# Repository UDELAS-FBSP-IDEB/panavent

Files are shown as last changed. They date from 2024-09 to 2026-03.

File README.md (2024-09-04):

# Panavent Project - An Open-Source Mechanical Ventilator.

This repository contains all the essential components for designing and implementing a mechanical ventilator. The central component is a gas mixer for mechanical ventilators, utilizing a multiloop and parallel PID controller system. The design and control system for the expiratory valve are also included, along with a C# application to manage the device's behavior, define various respiratory parameters, and display flow, volume, and pressure graphs.

The project provides a comprehensive solution, including hardware designs, control algorithms, 3D models, and complete source code for easy replication and further development.

## Project Structure

The repository is structured as follows:

- `/Electronics`: Contains electronic circuit schematics and hardware design files used in the gas mixer.
- `/3DModels`: 3D models and designs for the components used in the gas mixer.
- `/SourceCode`: The full code used for the control system, designed to run on the embedded platform.

## Features

- **Precise Gas Mixing**: Achieved using PID controllers in a multiloop and parallel configuration.
- **Open Source**: All designs, code, and models are provided as open-source materials.
- **Comprehensive**: Includes electronic design, mechanical components, and the full control algorithm.
- **Replicable**: All components can be replicated and adapted for various applications in medical settings.

## Requirements

- MPLAB X IDE and a PICkit programmer for executing the code of the microcontroller.
- Visual Studio 2017 or later for compiling and running the PC software.
- 3D printer for generating the physical components.
- Basic knowledge of PID control systems and electronics.
  
## License
This project is licensed under the MIT License, allowing for open-source distribution and adaptation. Please credit the original authors when using or adapting this work.

## Contact
For any questions or further information, feel free to reach out at luys.santana.0@udelas.ac.pa

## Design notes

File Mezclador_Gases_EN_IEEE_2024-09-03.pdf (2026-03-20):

Abstract-- Objective: To design and implement a gas mixer for mechanical ventilators using a system of PID controllers in multiloop and parallel configuration. Methods: The design process included addressing the theoretical principles of gas mixing by partial volumes and their relationship with mechanical ventilation parameters. The electro-pneumatic system of the mixer, the control system, and its implementation were developed and documented in detail. Results: The system's performance was
evaluated | through | experimental | tests, | and | the | results
demonstrated effective control and reliable gas mixing according to the set parameters. Conclusion: The proposed design successfully achieves the intended gas mixing for mechanical ventilators, ensuring accurate and consistent gas delivery. Significance: This work provides a comprehensive solution,
including | all | electronic | designs, | 3D | components, | and
programming code, contributing to the advancement of mechanical ventilation technology.

Index Terms-- Mechanical ventilation, gas mixer, PID
controllers, | multiloop | configuration, | parallel | control,
experimental prototype.
I. INTRODUCTION

The gas mixer in a mechanical ventilator plays a crucial role in preparing the therapeutic mixture of air and oxygen that is delivered to the patient during treatment. Its primary function is to accurately adjust the oxygen volume fraction (FiO2) in the inhaled gas mixture according to the specific needs of the patient. Additionally, the gas mixer actively participates in regulating the gas flow, taking into account parameters such as respiratory rate, airway pressure, and the set tidal volume. Precise control of these parameters is essential to ensure appropriate treatment, minimize the risks associated with
mechanical | ventilation, | and | ensure | the | successful
implementation of the therapeutic strategy defined by the attending physician [1], [2], [3].

The technical characteristics of the gas mixer are defined based on the specifications of the mechanical ventilator and its performance. In 2020, the World Health Organization suggested the minimum requirements for mechanical ventilators used in the treatment of acute respiratory diseases such as COVID-19 [4]; among these requirements, it is mentioned that an ICU mechanical ventilator should be able to regulate FiO2 between 21% and 100%, produce inspiratory flows from 1 to 160 L/min, and be compatible with both high and low-pressure oxygen sources. These requirements directly apply to the gas mixing module of the ventilator, as it is responsible for managing these aspects in the mechanical ventilator.

Given the importance of the gas mixer in a mechanical ventilator, numerous studies have focused on its optimization. Soares et al. [5] conducted a comprehensive review of the different types of gas mixers used in mechanical ventilators, highlighting the implementation of Proportional-Integral-Derivative (PID) controllers to regulate the air and oxygen mixture. Taube [6] describes an air and oxygen mixing system that uses a proportional solenoid valve, controlled by a microprocessor to automatically adjust the FiO2 according to the patient's blood oxygen saturation. Additionally, Taube [7] presents a system that not only mixes but also heats and humidifies the gases, with an adaptive PID control that adjusts the oxygen mixture delivered to the patient according to their needs. Radzi et. al [8] implemented a prototype that regulates the inspired oxygen fraction (FiO2) using proportional flow control valves for air and oxygen, integrating sensors that allow dynamic adjustment of the gas flow.

While gas mixing systems that use PID controllers are a well-established technology, there is limited documentation on the use of multiloop controllers in this context. This study describes the design and implementation of an advanced gas mixing system aimed at applications in mechanical ventilation. A system has been developed that employs PID controllers organized in a multiloop and parallel configuration, designed to keep the control functions of different hardware aspects separate, under the premise that this separation of roles optimizes the overall system's precision and stability. In this regard, our development focuses on independently managing the individual flow of each gas through the implementation of cascaded control subsystems, where the output of one controller serves as the input for the next. This approach aligns with previous research that has demonstrated the effectiveness of

Luys R. Santana, Manuel M. Batista, Sorhay M. Vásquez Biomedical Research and Development Center (IDEB) Faculty of Biosciences and Public Health, Universidad Especializada de las Américas (UDELAS), Paseo de la Iguana, Albrook, Panama City, Republic of Panama.

# Experimental prototype of an open-source gas mixer for mechanical ventilation based on PID controllers in

multiloop and parallel configuration.

dual systems in mechanical ventilation, where different loops effectively manage various respiratory parameters [9].

This document is structured as follows: first, the theoretical foundations of gas mixing are described, defining the mathematical framework that underpins the prototype. Next, the conceptual design is presented, and the control schemes used are explained. Then, the implementation of the device is detailed, along with its performance metrics. All electronic designs, 3D components, and the complete program code are provided. Finally, an exhaustive analysis of the obtained results is offered.

II. THEORETICAL FOUNDATIONS OF GAS MIXING
Amagat's Law of Partial Volumes states that in a mixture of gases, the total volume of the mixture is equal to the sum of the individual volumes of each of the gases that make up the mixture, as if they were coexisting separately at the same temperature and pressure [10]. Mathematically, it is expressed as:

Vt = ∑ Vi

n
i=1 = V1 + V2 + ⋯ + Vn

1 = ∑

Vi
Vt

n
i=1

(1)

where Vt
corresponds to the total volume in the mixture of n gases. Consequently, the volume of each gas corresponds to a fraction of the total volume, such that their sum equals one.

In this context, air itself constitutes a mixture of different gases, with oxygen present at a concentration of 21% (typically at sea level), along with other gases such as nitrogen and argon, which together make up the remaining 79%. Applying equation (1), we can represent this mixture as follows:

VM = 0.79VM + 0.21VM | (2)

where VM is the total volume of the mixture, 0.21VM is the total volume of oxygen, and 0.79VM is the volume of the other components.

If one wished to prepare a mixture of oxygen-enriched air (air that receives an additional supply of oxygen) with a total volume VM and an arbitrary oxygen concentration CM defined in the range 0.21 ≤ CM ≤ 1, it would be understood that:

VM = 0.79Vair + Vto2
(4)

where Vair is the volume of air added to the mixture and Vto2 is the total volume of oxygen:

Vto2 = 0.21Vair + Vo2
(5)

where Vo2
is the volume of additional pure oxygen.

On the other hand, by applying equation (2), it can be deduced that the oxygen concentration CM in the mixture VM is given by:

CM =

Vto2
VM

(6)

so that:

Vto2 = CM. VM | (7)

The concentration of the other gases would be given by:

0.79Vair = (1 − CM)VM

Vair =

(1−CM)VM
0.79 | (8)

while the volume of oxygen Vo2 :

Vto2 = 0.21Vair + Vo2 = CMVM

Vo2 = CMVM − 0.21Vair | (9)

Directly measuring the volume can be impractical in this type of application, so we could redefine these formulas in terms of flow if we consider that VM must be delivered during the inspiratory phase of ventilation, which has a duration Ti .
Thus, we can define a target flow FM as:

FM =

VM Ti | (10)

and consequently, the air flow Fair and oxygen flow Fo2 required to generate the mixture:

Fair =

(1−CM)FM
0.79

(11)

FO2 = CMFM − 0.21Fair | (3)

Based on this, a gas mixer by partial volumes for a mechanical ventilator requires a method to control the flows of air and oxygen that are combined and delivered to the patient during the inspiratory phase of ventilation, and it must be able to repeat this process accurately with each breath.

III. PID CONTROLLER
The expression that defines the response of a PID (Proportional-Integral-Derivative) controller is determined by the following formula:

### u(t) = Kpe(t) + Ki ∫ e(t)dt + Kd

de(t)
dt
[11] (13)

where Kp, Ki y Kd are the proportional, integral, and derivative coefficients of the system, respectively.

The function e(t) is the error, defined as the difference between the desired value m(t) and the measured value l(t):

e(t) = m(t) − l(t) | (14)

On the other hand, applying the Laplace transform to equation (13), we obtain the transfer function:

U(s)
E(s)

= Kp +

Ki
s
+ Kds | (15)

IV. CONCEPTUAL DESIGN

A gas mixer with cascaded PID controllers is proposed, where the output of the first controller serves as the input for the next internal controller. Figure 1 shows the functional model of the proposed gas mixer. The system consists of four
(4) PID controllers in a multi-loop configuration, responsible for regulating the flow of each gas at an individual level: two PID controllers are located in the subsystem Sa (which controls the air supply) and two more in So (which controls the oxygen supply). These subsystems operate in parallel. The subscripts e, m, and l represent the error, the target value, and the measured value, respectively.

In figure 1, Cm y Fm are input parameters to the mixer coming from the ventilator, representing the target concentration and target flow, respectively. These parameters are used to determine the individual flows of air and oxygen using equations (11) and (12). This is represented by the block f(Fm , Cm). Then, each resulting target flow value is processed separately in the identical subsystems Sa and So.

Figure 2 shows the internal composition of each subsystem. The input controller PIDf regulates the gas flow coming from the high-pressure source (air or oxygen). The parameter fm corresponds to the target flow calculated in the block f(Fm , Cm), meaning Fair or Fo2 as applicable, and fl
to the measured flow.

The output Im from PIDf serves as the input to the PIDi controller, whose purpose is to regulate the current in a proportional valve, which in turn determines the gas flow supplied. Since in proportional valves the flow intensity is proportional to the current, the objective of this subsystem is to keep the current close to a target value (Im), which corresponds to the desired calculated flow. In this way, PIDi converts Im into the signal Oi which is sent to the physical valve control system Ec
, i.e., the electronic circuit, and finally to the valve.

By applying equation (13) to PIDf, the target current Im that must be supplied to the valve is obtained:

Im(t) = Kpfe

(t) + Ki ∫ fe
(t)dt + Kd

df
dt

(16)

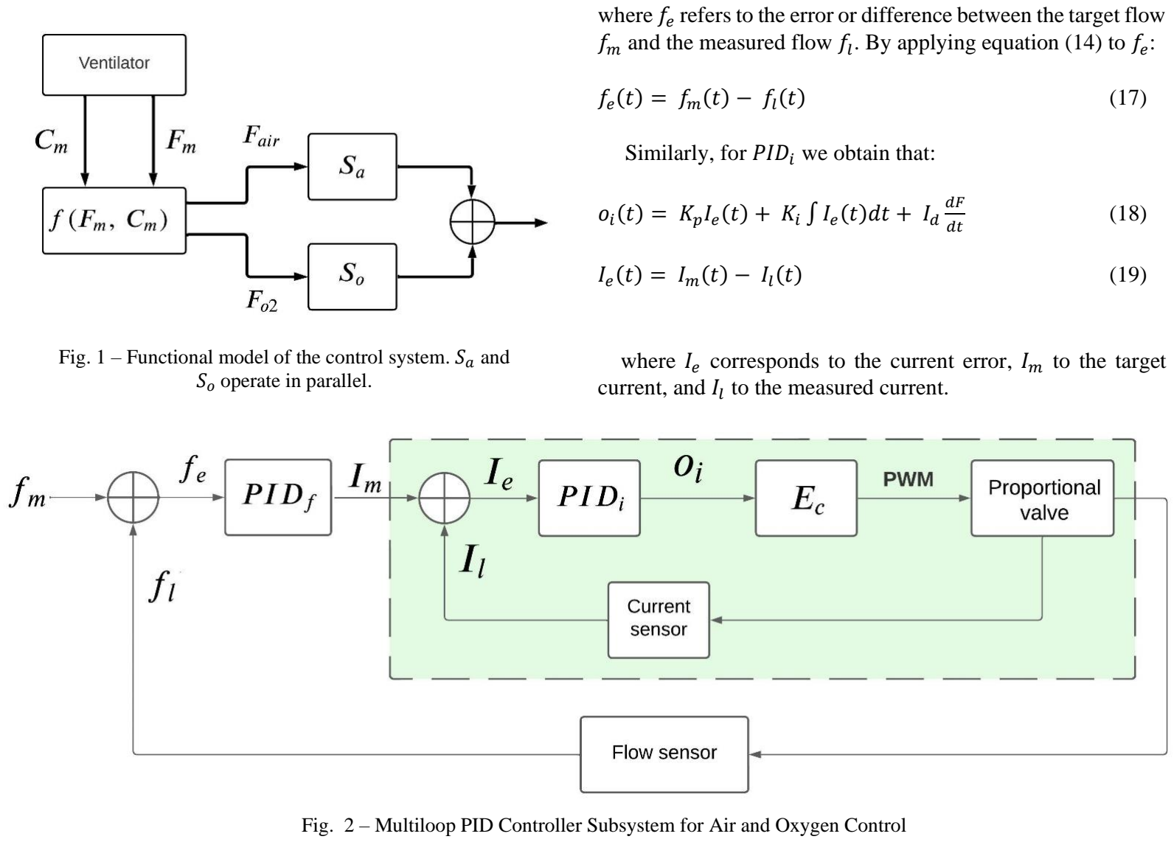
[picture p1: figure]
where fe fm and the measured flow fl; . By applying equation (14) to fe; Similarly, for PIDi we obtain that:; (t) = KpIe; current, and Il; to the measured current.; So operate in parallel.

refers to the error or difference between the target flow

where Ie corresponds to the current error, Im to the target

Fig. 1 – Functional model of the control system. Sa and

Fig. 2 – Multiloop PID Controller Subsystem for Air and Oxygen Control

Finally, the outputs of both subsystems are combined, directing the resulting gas flow to the patient, where the oxygen concentration is measured.

V. IMPLEMENTATION

Figure 3 shows the developed pneumatic system, and Figure 4 presents the electronic board designed according to the proposed design. The electronic schematics, software, blueprints, and drawings are available in the GitHub repository of IDEB for the Panavent project [12].

A. Pressure Regulators and Sensors

The objective of the regulators is to ensure that the working pressure remains within the tolerance limits of the flow sensors and proportional valves. According to the NFPA 99 standard, the output pressure in medical gas installations (such as oxygen, medical air, nitrogen, etc.) must be regulated to 50 psi, so the design was carried out considering this criterion.

The OxyReg model POR234KM1250 regulator was used. This device allows a maximum flow of 700 l/min, tolerates input pressures of up to 260 psi, and provides a stable output of 50 psi [13].

To monitor the pressure of the gases entering the system, two Honeywell SSCMANN006BGAA3 sensors [14] were used to provide feedback to the control system and generate alarms. This is crucial because the performance of certain devices, such as proportional valves, depends on the operating pressure, which must be maintained within the limits defined by the manufacturer.

B. Input Flow Sensors

Two Sensirion SFM4200 [15] flow sensors were used, one for each gas. This is a digital sensor with I2C output, internally linearized, and with integrated temperature compensation. Its measurement range is from 0 to 160 slm, and it can operate at a maximum pressure of 8 bar (approximately 116 psi), with an accuracy of 2.5% to 5% of the measured value and a repeatability of 0.02% within its measurement range. This sensor was selected due to its performance characteristics in high-pressure applications.

The original structure of the sensor was partially modified. The gas inlet and outlet couplings were replaced with 3D-printed parts to adapt them to the manifold of the proportional valves on one side and to the gas inlets on the other. To prevent gas leaks, each coupling is fitted with a double rubber ring or O-ring. This is illustrated in figure 5.

C. Proporcional valves

To control the flow of each gas, two proportional valves were selected. These valves consist of a coil wound around a metal plunger, designed in such a way that it can move in and out of its casing, operating the valve's opening and closing mechanism. Due to their inductive nature, when a voltage is applied across the coil terminals, the current flow begins to increase gradually, generating a magnetic field. Once the

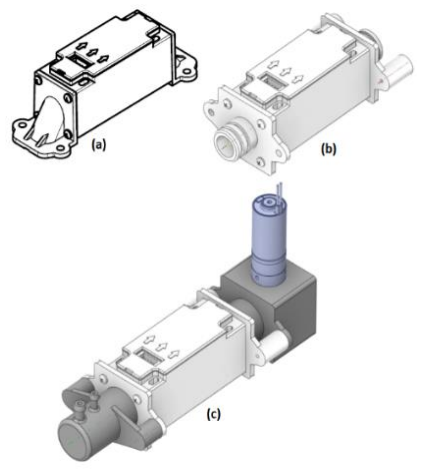
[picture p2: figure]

Fig. 5 – Flow Sensor Modifications: (a) the sensor as shown in the datasheet, (b) modifications made, (c) the sensor coupled to the valve manifold (right) and the inlet

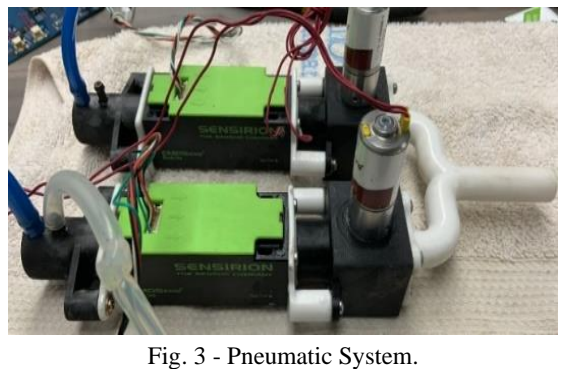
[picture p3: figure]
Fig. 3 - Pneumatic System.
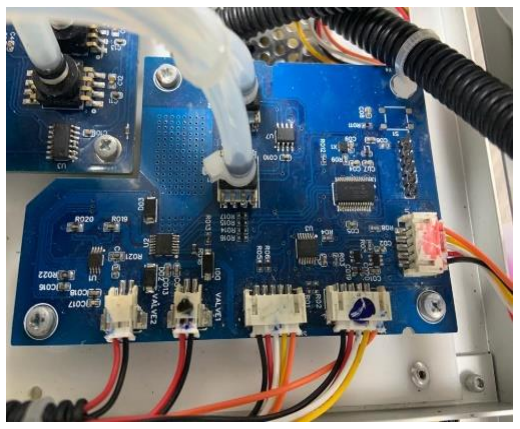
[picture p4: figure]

nozzle (left). Fig. 4 - Electronic System.

magnetic field reaches sufficient strength, an electromotive force is produced that displaces the plunger, allowing gas to flow through the valve. Therefore, the flow is regulated by controlling the current passing through the solenoid coil: the higher the current, the greater the gas flow, and vice versa [16].

As a tool for selecting the manufacturer and model of the valve, four evaluation criteria were defined:

1. Ability to supply the target flow FM at the maximum and minimum extremes of Vt and Ti
, evaluating equation
(10.)
2. High repeatability in valve positioning, meaning reasonably low hysteresis.
3. Low power consumption.
4. Seat or seal compatible with oxygen.

The model DV-PM-10-600050-V valve [17], manufactured by Clippard, was selected. This valve offers a performance of 60 l/min at an input pressure of 50 psi, notable for its high linearity and very low hysteresis. The seal material is fluorinated rubber (FKM), suitable for handling medical oxygen according to ASTM International standard D1418 [18]. The valve was mounted on a 3D-printed manifold using biocompatible resin. The valve was secured to the manifold using a metal insert.

D. Static Mixer

After the proportional valves, an in-line static mixer was placed to homogenize the mixture. The mixer has a diameter of 5.5 mm, a length of 58 mm, and contains 3 blades, each 19.5 mm long. The blades are arranged in such a way that they alternate 180-degree turns to the right and left, so that the front end of one blade is perpendicular to the rear end of the next. The opposing direction of rotation for each blade maximizes the mixing effect [19].

E. Microcontroller and Firmware

The dsPIC33CK32MC102 microcontroller (µC) [20] was used as the central processing unit, and it was programmed in C using MPLAB X IDE v6.05 [21].

The system clock was programmed to operate at a frequency of 120 MHz using an external 10 MHz MEMS resonator (DSC1001DL5-010.0000 [22]), utilizing the built-in PLL module of the microcontroller.

This code was modified to include a timeout routine in the I2C module, allowing the system to exit the wait loop in case of communication bus errors, such as when a slave device holds the SCL line low due to a malfunction, electrical fluctuations, or a poor connection. Additionally, a routine was implemented to forcibly recover the I2C bus in the event of a collision. Furthermore, drivers were developed to manage the shared use of timers 1 and 3, along with interfaces to handle various devices in the circuit, including I2C gates, external ADCs, and

Sensirion SFM flow sensors. All of this is integrated into the "panavent.hardware.drivers" library.

On the other hand, the logic of the gas mixer was implemented in the "panavent.mezclador" library. This is where the code that performs the calculations for preparing the mixture and reads all the sensors involved in the process is located. The library is designed in such a way that it can be incorporated as a reference or module into the main program.

The mixing process is executed by invoking the “mezclar” function from the "panavent.mezclador" library, which receives the target flow and target concentration defined by the user as input parameters. This function should be invoked in a loop with a period no less than 1 ms, the time required for all involved devices to respond appropriately, especially the flow sensors [15].

The source code for the PID controllers is located in the "panavent.utilities" library. The implemented algorithm incorporates an EMA filter to smooth fluctuations in the derivative component. Additionally, the controller's output is restricted to a configurable range to prevent overflow caused by integral accumulation.

F. Operation

The main program invokes the "mezclar" function with the target concentration and flows provided by the ventilator (user). With this data, equations (11) and (12) are applied to calculate
Fair and FO2

. After this, the subsystems Sa and So are executed, where equations (16) and (18) are calculated.

Subsequently, the microcontroller sends a PWM signal to each channel of the high-side power switch ITS4040D-EP-D (each channel is connected to a proportional valve) with a duty cycle proportional to equation (18). During the high part of the PWM signal, the valve's inductor accumulates energy and conducts current. When the PWM cycle switches to the low part, the switch opens the circuit, and the solenoid discharges through the freewheeling diodes (D02 and D03) and the current sensing resistor. In this way, an average current proportional to the duty cycle is applied to the inductor.

To measure the current flowing through the valves, a 0.1 Ohm resistor is used for each channel (R19 and R20). This resistor is deliberately low to minimize its impact on circuit performance, particularly on the solenoid's charging time. The ends of the resistor are connected to the differential inputs of the operational amplifier INA2290A3IDGKT (U1), so that the voltage drop is sensed and amplified. A filter was placed at the output of U1 to reduce the ripple caused by the PWM before sending it to the microcontroller, where the current is calculated by applying Ohm's law. This current serves as the input to PIDi ,
allowing it to calculate the appropriate output.

VI. PID CONTROLLER TUNING

The tuning of the controllers was carried out using the classic Ziegler-Nichols method to ensure optimal adjustment of the proportional, integral, and derivative parameters, applying the closed-loop response rule with no-overshoot (NO-OV) as detailed in [23]. The proportionality coefficients obtained for the controllers are shown in Table II.

The measurements were taken using a 200 MHz Siglent oscilloscope and a Fluke VT650 gas analyzer (Fig. 6), both of which had been calibrated within the last year.

To tune PIDi
the voltage at the output of the current sensing circuit, i.e., at the input of the microcontroller's ADC, was measured. For tuning the other controllers, the flow at the output of the pneumatic system was measured.

VII. PID PERFORMANCE METRICS

To evaluate the performance of each PID controller, the following key indicators (performance metrics) were recorded in response to a step signal [6]:

- Steady-State Value (SS): This is the final value reached by the system's output, which remains constant after a period of time under constant input conditions.
- Percent Error: The percentage difference between the steady-state value and the target value.
- Rise Time (Tr): The time it takes for the system's output to go from 10% to 90% of the steady-state value.
- Settling Time (Ts): The time it takes for the system's output to reach and stay within a ±5% band around the steady-state value.
- Overshoot (Ov): The difference between the maximum value reached by the output and the steady-state value. In tables where overshoot is not shown, its value was close to 0% of the final value, so it was omitted.

The procedure used for the calculation and measurement of each performance metric was as follows:

1. A target value (fm or Im) was defined and applied to the PID controller as one of its inputs.
2. The input was maintained for 2 seconds, during which the controller's output data was captured using one of the aforementioned measurement instruments. Then, the input was set to 0 for an additional 2 seconds.
3. This process was repeated 10 consecutive times (10 steps).
4. The measurements generated by the instrument were exported.
5. The key indicators for each step were calculated and averaged. This process was performed using the “Analyzer.cs” script [12], specifically designed for this purpose.
6. This process was repeated using a new target value.

Figure 7 shows the step response graph of the PIDi controller, and Table III details the performance metrics at different target current values Im.

Figure 8 shows the step response graph of the flow controller PIDf
and Table IV details the performance metrics at different target flow values fm.
TABLE II. | PID PROPORTIONALITY COEFFICIENTS
Controller | Kp | Ki | Kd
PIDi | 5.0 | 300.1852 | 0.022
PIDf | 0.0015 | 0.025 | 0.00003

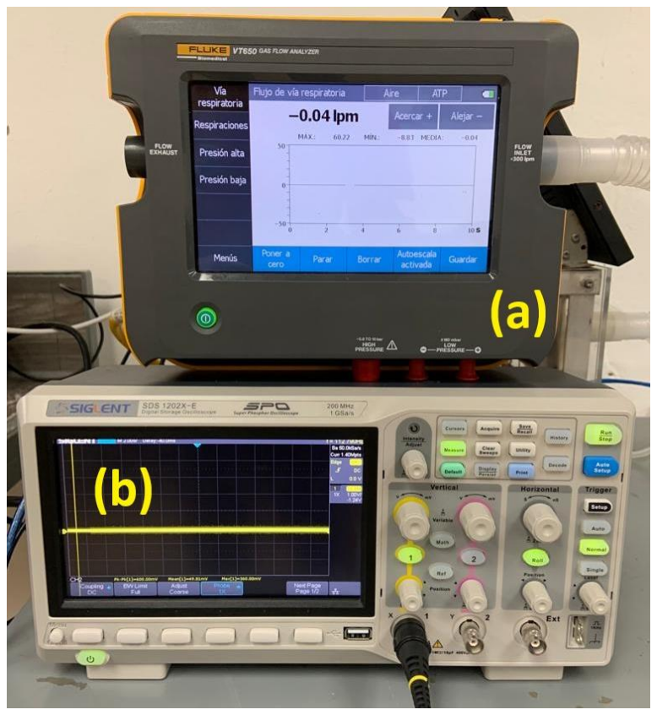
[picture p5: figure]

Fig. 6 – (a) Siglent 200MHz oscilloscope and (b) Fluke VT650 flow analyzer, used to make the measurements.

TABLA III. | PIDi PERFORMANCE METRICS
Im (A) | SS | % Error | Tr (ms) | Ts (ms)
0.10 | 0.098208 | 1.79 | 34.04 | 38.22
0.11 | 0.107781 | 2.02 | 33.27 | 38.89
0.12 | 0.118005 | 1.66 | 26.53 | 30.08
0.13 | 0.127449 | 1.96 | 25.14 | 29.34
0.14 | 0.137080 | 2.09 | 23.85 | 28.02
0.15 | 0.147032 | 1.98 | 22.64 | 26.22
0.16 | 0.156727 | 2.05 | 24.18 | 26.95
0.17 | 0.166653 | 1.97 | 22.28 | 26.18
0.18 | 0.176432 | 1.98 | 18.05 | 19.42
0.19 | 0.186067 | 2.07 | 16.03 | 21.62

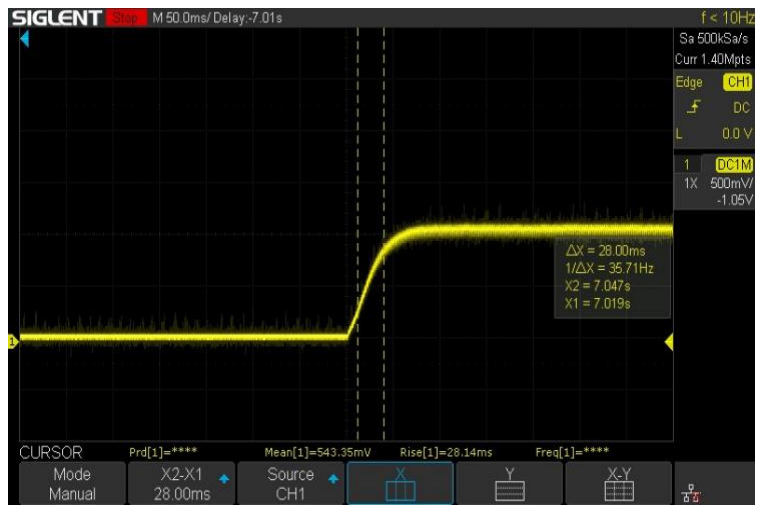
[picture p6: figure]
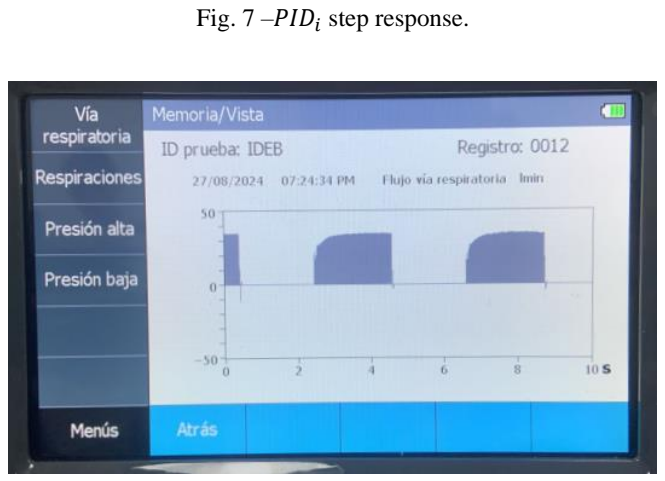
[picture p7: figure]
Fig. 7 –PIDi; step response.

VIII. GAS MIXER PERFORMANCE METRICS

To evaluate the efficiency of the system as a whole, oxygen concentration measurements were taken under different operating conditions. The results obtained are presented in Table V. The procedure followed for these measurements was as follows:

1. The gas analyzer VT650 was connected to the system's output.
2. A target flow value Fm (starting with 10 L/min) and a target concentration value Cm (starting with 25%) were set.
3. A 20-second wait period was observed to allow the oxygen sensor of the analyzer to reach equilibrium.
4. The measured oxygen concentration was recorded.
5. Steps 2-4 were repeated with different combinations of Fm and Cm.

IX. RESULTS AND DISCUSSION

The PIDi controller shows consistent performance across the entire operating range, with low percentage errors and fast response times:

- The steady-state value improves as the target current increases, which is especially beneficial when controlling a high gas flow.
- The percentage error varies slightly between 1.66% and 2.09%, with a mean deviation of 0.093% and a standard deviation of 0.127%. These are relatively low values, indicating that the controller is quite accurate. Additionally, the low dispersion of percentage errors around the mean suggests that the PIDi controller has uniform performance across its entire operating range.
- The rise time (Tr) decreases as Im increases, from 34.04 ms to 16.03 ms. This behavior is favorable, as a shorter rise time means the system reaches the target value more quickly. Moreover, this indicates that the controller becomes more responsive at higher currents, which is advantageous in situations requiring a rapid response.
- Similar to Tr, the settling time (Ts) decreases as Im increases, indicating better stability and quicker achievement of the steady state, which is indicative of a system that stabilizes relatively quickly after a change in input.

Regarding the PIDf controller, it stands out for its good accuracy in tracking the target flow, maintaining low percentage errors throughout its entire operating range. However, a slight decrease in performance is observed as the flow increases:

- The percentage error slightly decreases as fm increases, reaching its lowest value (0.23%) at 25 L/min. After this point, the percentage error slightly increases again, reaching 0.61% at 40 L/min. Overall, the percentage errors remain low, with a reduced mean deviation (0.1%) and standard deviation (0.12%), indicating that the controller maintains high accuracy and minimal variability in flow regulation across its entire operating range.
- The overshoot increases with the rise in fm, going from 0.29% to 0.86%. Although the overshoot values remain relatively low, this increase indicates that the system tends to slightly exceed the target value before stabilizing, especially at higher flows.
TABLA IV. | PIDf PERFORMANCE METRICS
fm (l/min) | SS | Ov. | % Error | Tr (ms) | Ts (ms)
10.00 | 9.94 | 0.29 | 0.61 | 253.09 | 355.75
15.00 | 14.94 | 0.34 | 0.37 | 369.85 | 513.64
20.00 | 19.92 | 0.45 | 0.41 | 406.07 | 550.50
25.00 | 24.94 | 0.67 | 0.23 | 430.57 | 562.03
30.00 | 29.87 | 0.69 | 0.45 | 437.67 | 590.18
35.00 | 34.83 | 0.86 | 0.49 | 469.86 | 653.38
40.00 | 39.75 | 0.71 | 0.61 | 536.37 | 749.13

Fig. 8 –PIDf step response.

- The rise time and settling time consistently increase with the rise in fm. This suggests that the system requires more time to reach 90% of the steady-state value at higher flows.

On the other hand, the overall performance metrics of the system indicate that the gas mixer operates with acceptable efficiency and precision:

- The average concentration calculated for each combination of target flow Fm and target concentration Cm is quite close to the target value. This suggests that the gas mixer is operating with high accuracy under most of the evaluated conditions.
- The average concentrations align well with the target
concentrations, | especially | in | higher | flow | and
concentration ranges, which is a good indication of the system's stability and reliability.
- The absolute error ranges from 0.40 to 1.06, indicating a good level of precision in gas mixing. The highest errors are observed at lower Cm concentrations, which may suggest that the system is slightly less accurate in these ranges. However, even the highest absolute error of 1.06 is still relatively low, indicating that the gas mixer maintains overall good precision.
- The percentage error ranges from 0.44% to 4.23%, being higher at lower target concentrations (25.00%) and decreasing as the target concentration increases. This behavior suggests that the system is more efficient in controlling mixtures with higher oxygen concentrations. The generally low percentage error reinforces the idea that the system is well-tuned and capable of providing accurate gas mixtures under a variety of operating conditions.
- The standard deviation ranges from 0.08 to 0.48, indicating variability in the mixer's precision depending on the target flow and concentration. Higher standard deviations in high flows and elevated concentrations might suggest slight fluctuations in system performance under these conditions. However, most standard deviations are quite low, indicating reasonable consistency in the system's precision.
X. CONCLUSIONS

The analysis of the system reveals a robust and efficient design, suitable for applications in mechanical ventilation. The multiloop PID controllers, both for current and flow, demonstrated high performance in step response, with low percentage errors and minimal variability.

Additionally, the gas mixer performance metrics, measured through oxygen concentration under various conditions, confirm that the system maintains high precision in regulating mixtures. This is evidenced by the overall operation of the system with reduced standard deviation, indicating consistent and reliable performance.

Overall, the designed gas mixing system proves to be efficient and precise. However, optimizing performance under extreme flow and concentration conditions could further enhance the system's reliability in high-demand situations.

TABLA V. | GAS MIXER PERFORMANCE METRICS
| Target flow Fm(L/min)
10 | 15 | 20 | 25 | 30 | 35 | 40 | Avg. | Error | % Error | σ
| 25.00 | 26.10 | 26.10 | 26.10 | 26.00 | 26.10 | 26.10 | 25.90 | 26.06 | 1.06 | 4.23 | 0.08
| 30.00 | 30.40 | 30.80 | 31.10 | 30.80 | 30.90 | 30.90 | 31.00 | 30.84 | 0.84 | 2.81 | 0.22
| 35.00 | 35.90 | 35.80 | 35.90 | 35.70 | 35.70 | 35.90 | 35.90 | 35.83 | 0.83 | 2.37 | 0.10
| 40.00 | 40.10 | 40.70 | 40.80 | 40.80 | 40.70 | 40.80 | 40.80 | 40.67 | 0.67 | 1.68 | 0.26
| 45.00 | 45.30 | 45.80 | 45.80 | 45.70 | 45.50 | 45.50 | 45.70 | 45.61 | 0.61 | 1.37 | 0.19
| 50.00 | 50.10 | 50.70 | 50.60 | 50.60 | 50.50 | 50.40 | 50.50 | 50.49 | 0.49 | 0.97 | 0.20
| 55.00 | 55.20 | 55.60 | 55.60 | 55.60 | 55.40 | 55.40 | 55.20 | 55.43 | 0.43 | 0.78 | 0.18
| 60.00 | 60.10 | 60.50 | 60.60 | 60.60 | 60.50 | 60.40 | 60.20 | 60.41 | 0.41 | 0.69 | 0.20
| 65.00 | 65.20 | 65.40 | 65.60 | 65.70 | 65.40 | 65.40 | 65.20 | 65.41 | 0.41 | 0.64 | 0.19
| 70.00 | 70.20 | 70.20 | 70.50 | 70.60 | 70.50 | 70.40 | 70.20 | 70.37 | 0.37 | 0.53 | 0.17
| 75.00 | 75.90 | 75.40 | 75.40 | 75.40 | 75.40 | 75.30 | 75.10 | 75.41 | 0.41 | 0.55 | 0.24
| 80.00 | 81.10 | 80.60 | 80.50 | 80.10 | 80.20 | 80.10 | 80.10 | 80.39 | 0.39 | 0.48 | 0.38
| 85.00 | 86.10 | 86.10 | 85.80 | 85.80 | 85.50 | 85.00 | 85.90 | 85.74 | 0.74 | 0.87 | 0.39
| 90.00 | 91.10 | 90.80 | 90.60 | 90.40 | 90.10 | 90.10 | 89.70 | 90.40 | 0.40 | 0.44 | 0.48
| 95.00 | 95.70 | 95.80 | 95.70 | 95.40 | 95.20 | 95.20 | 95.10 | 95.44 | 0.44 | 0.47 | 0.29

Target concentration

Cm (%)

XI. ACKNOWLEDGMENTS

This work is a derivative research project from Panavent (COVID19-P-228), funded by the National Secretariat of Science and Technology (SENACYT) of the Republic of Panama, through the emergency funding program for research projects during the COVID-19 pandemic.

XII. REFERENCES

[1] S. Sood, H. A. Ganatra, F. Perez Marques, and T. R.
Langner, | “Complications | during | mechanical
ventilation—A pediatric intensive care perspective,”
Feb. | 01, | 2023, | Frontiers | Media | S.A. | doi:
10.3389/fmed.2023.1016316.
[2] A. Serpa Neto et al., “Association Between Use of Lung-Protective Ventilation With Lower Tidal Volumes and Clinical Outcomes Among Patients Without Acute Respiratory Distress Syndrome A Meta-analysis,” 2012. [Online]. Available: http://www.jama
[3] J. Guay, E. A. Ochroch, and S. Kopp, “Intraoperative use of low volume ventilation to decrease postoperative mortality, mechanical ventilation, lengths of stay and lung injury in adults without acute lung injury,” Jul. 09,
2018, | John | Wiley | and | Sons | Ltd. | doi:
10.1002/14651858.CD011151.pub3.
[4] World Health Organization, “Technical specifications for invasive and non-invasive ventilators for COVID-19,” 2020. Accessed: Jun. 14, 2023. [Online]. Available:
https://apps.who.int/iris/handle/10665/331792
[5] G. F. Soares, O. M. Almeida, J. W. M. Menezes, S. S.
A. Kozlov, and J. J. P. C. Rodrigues, “Air–Oxygen Blenders for Mechanical Ventilators: A Literature
Review,” | Mar. | 01, | 2022, | MDPI. | doi:
10.3390/s22062182.
[6] J. Taube, “Solenoid Air/Oxygen System for Use with an Adaptive Oxygen Controller and Therapeutic Methods of Use,” Jul. 2008.
[7] J. C. Taube, “Oxygen Mixing and Delivery,” Dec. 2019.
[8] M. F. Radzi, H. M. Saputra, C. H. A. H. B. Baskoro, M. Mirdanies, R. I. A. Aziz, and N. Ismail, “PID-Based Fraction of Inspired Oxygen (FiO2) Control System in ICU Ventilator,” in 2021 IEEE 7th International Conference on Smart Instrumentation, Measurement and Applications, ICSIMA 2021, Institute of Electrical and Electronics Engineers Inc., Aug. 2021, pp. 185–
189. doi: 10.1109/ICSIMA50015.2021.9525942.
[9] F. Tehrani et al., “A DUAL CLOSED-LOOP
CONTROL | SYSTEM | FOR | MECHANICAL
VENTILATION,” 2004.
[10] Yunus Cengel and Michael Boles, “Thermodynamics: An Engineering Approach 8th Edition,” 2014.
[11] D. E. Seborg, T. F. Edgar, D. A. Mellichamp, and F. J. Doyle III, “Process Dynamics and Control Fourth Edition,” 2016.
[12] UDELAS-FBSP-IDEB, “Panavent,” 2024. Accessed:
Aug. | 30, | 2024. | [Online]. | Available:
https://github.com/UDELAS-FBSP-IDEB/panavent
[13] Proportion Air, “OxiReg, Pressure Regulation for Medical Applications.” Accessed: Jun. 15, 2023.
[Online]. | Available: | https://proportionair.com/wp-
content/uploads/2020/07/Safety-Regulators-OXYREG.pdf
[14] Honeywell International Inc, “TruStability Silicon Pressure Sensors: SSC Series-Standard Accuracy
Analog.” | [Online]. | Available:
www.honeywell.com/sensing
[15] Sensirion, “Preliminary datasheet SFM4200 Digital Flow Meter for Air and Oxygen.” [Online]. Available: www.sensirion.com
[16] Texas Instruments, “Reference Design for Automotive,
Proportional-Solenoid | Current | Sensor,” | 2017.
Accessed: Aug. 20, 2024. [Online]. Available: https://www.ti.com/lit/pdf/tidudf9
[17] Clippard Instrument Laboratory, “DVP High Flow Proportional Control Valves datasheet.” Accessed:
Aug. | 20, | 2024. | [Online]. | Available:
https://www.clippard.com/downloads/PDF_Documents/Product%20Data%20Sheets/Clippard%20DVP%20 High%20Flow%20Proportional%20Valve.pdf
[18] ASTM International, “Standard Practice for Rubber and Rubber Latices—Nomenclature,” 2022. Accessed:
Aug. | 20, | 2024. | [Online]. | Available:
https://webstore.ansi.org/standards/astm/astmd141822
[19] A. Ghanem, T. Lemenand, D. Della Valle, and H.
Peerhossaini, | “Static | mixers: | Mechanisms,
applications, and characterization methods–A review,” Chemical Engineering Research and Design, vol. 92,
no. | 2, | pp. | 205–228, | 2014, | doi:
10.1016/j.cherd.2013.07.013.
[20] Microchip Technology, “High-Performance 16-Bit DSP RISC CPU datasheet.” Accessed: Jun. 15, 2023.
[Online]. | Available:
https://www.mouser.com/datasheet/2/268/dsPIC33CK64MC105_Family_Data_Sheet_DS70005399C-1894321.pdf
[21] Microchip Technology, “MPLAB X IDE v6.05,” v6.05. Accessed: Jun. 15, 2023. [Online]. Available: https://www.microchip.com/en-us/tools-resources/develop/mplab-x-ide
[22] Microchip Technology, “DSC1001/3/4 datasheet.”
[23] A. S. McCormack and K. R. Godfrey, “Rule-based autotuning based on frequency domain identification,” IEEE Transactions on Control Systems Technology, vol. 6, no. 1, pp. 43–61, 1998, doi: 10.1109/87.654876.

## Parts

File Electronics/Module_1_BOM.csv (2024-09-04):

ID | Name | Designator | Footprint | Quantity | Manufacturer Part | Manufacturer
1 | 2.2uF | C01 | C0603 | 1 | CL10A225KQ8NNNC | Samsung Electro-Mechanics
2 | 4.7uF | C02,C015,C016 | C0603 | 3 | JMK107BJ475KAHT | Taiyo Yuden
3 | 100nF | C03,C04,C05,C07,C09,C010,C011,C012,C014,C017 | C0603 | 10 | 0603YC104JAT2A | AVX
4 | 10uF | C06 | C0603 | 1 | CL10A106MP8NNNC | SAMSUNG
5 | 470pF | C08 | C0603 | 1 | 500R14W471KV4T | Johanson Dielectrics
6 | 22nF | C013,C018 | C0603 | 2 | CGJ3E2X7R1H223K080AA | TDK
7 | 1uF | C019 | CAPC1608X90N | 1 | TMK107BJ105KA8T
8 | 1uF | C020 | CAPC1608X90N | 1
9 | S1A-13-F | D01 | SMA_L4.4-W2.8-LS5.4-RD | 1 | S1A-13-F | DIODES
10 | SL12-E3/5AT | D02,D03 | SMA_L4.3-W2.6-LS5.2-RD | 2 | SL12-E3/5AT | Diodes Incorporated
11 | Header-Male-2.54_1x6 | ICSP | HDR-TH_6P-P2.54-V-M-1 | 1 | Header-Male-2.54_1x6 | BOOMELE
12 | 620105131822 | J1,SF1,SF2 | 620105131822 | 3
13 | MH1608-601Y | L1 | L0603 | 1 | MH1608-601Y | BOURNS
14 | SSCMANN006BGAA3 | P1,P2 | SSCMANN006BGAA3 | 2
15 | 10K | R01,R02,R05,R06,R014,R015,R016,R017 | R0603 | 8 | CRCW060310K0JNEA | Vishay Intertech
16 | 1.5K | R03,R04,R07,R08 | R0603 | 4 | RC0603FR-071K5L | YAGEO
17 | 75 | R09 | R0603 | 1 | WR06X75R0FTL | WALSIN
18 | 0 | R010,R012 | R0603 | 2 | ERJ-3GEY0R00V | PANASONIC
19 | 10K | R011 | R0603 | 1 | ERJ-3EKF1002V | PANASONIC
20 | 100K | R013 | R0603 | 1 | CMP0603AFX-27R0ELF | Bourns
21 | 2.2k | R018 | RESC1608X55N | 1 | RT0603FRD072K2L
22 | 0.1 | R019,R020 | R0805 | 2 | CRM0805AFX-R100ELF | Bourns
23 | 1k | R021,R022 | R0805 | 2 | CHP0805AFX-1001ELF | Bourns
24 | 430182043816 | S1 | 430182043816 | 1
25 | INA2290A3IDGKT | U1 | VSSOP-8_L3.0-W3.0-P0.65-LS5.0-BL | 1 | INA2290A3IDGKT | TI
26 | ITS4040D-EP-D | U2 | PG-TSDSO-14_L4.9-W3.9-P0.65-LS6.0-BL-EP | 1 | ITS4040D-EP-D | Infineon Technologies
27 | PCA9543APW | U3 | TSSOP-14_L5.0-W4.4-P0.65-LS6.4-BL | 1 | PCA9543APW | NXP
28 | R1191N033B-TR-FE | U4 | SOT-23-5_L2.9-W1.6-P0.95-LS2.8-TL | 1 | R1191N033B-TR-FE | RICOH Electronic Devices Co., LTD.
29 | MCP1703T-5002E/CB | U5 | SOT-23-3_L2.9-W1.3-P1.90-LS2.4-BR | 1 | MCP1703T-5002E/CB | MICROCHIP
30 | MCP3426A0-E/SN | U7 | SOIC-8_L4.9-W3.9-P1.27-LS6.0-BL | 1 | MCP3426A0-E/SN | Microchip Tech
31 | dsPIC33CK32MC102_SSOP | U8 | DSPIC33CK32MC102_SSOP | 1 | DSPIC33CK32MC102-I/SS | Microchip Technology
32 | 2-292173-2 | VALVE1,VALVE2 | CONN-SMD_2-292173-2 | 2 | 2-292173-2 | TE Connectivity
33 | DSC1001DL5-010.0000 | X1 | OSC-SMD_4P-L2.5-W2.0-BL-A | 1 | DSC1001DL5-010.0000 | MICROCHIP(美国微芯)

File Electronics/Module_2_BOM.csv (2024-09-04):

ID | Name | Designator | Footprint | Quantity | Manufacturer Part | Manufacturer
1 | 2.2nF | C1 | C1206 | 1 | 12061C222KAT2A | AVX
2 | 100nF | C2,C4,C7,C8,C9,C10,C11,C13,C15,C17 | C0603 | 10 | 0603YC104JAT2A | AVX
3 | 10uF | C3 | C0603 | 1 | CL10A106MP8NNNC | SAMSUNG
4 | 47pF | C5,C6 | CAPC1608X90N | 2 | 0603YC470KAT2A | KYOCERA AVX
5 | 470pF | C12,C14 | C0805 | 2 | 08052A471FAT2A | AVX
6 | 10nF | C16 | C0603 | 1 | 06035C103K4Z2A | AVX
7 | 22nF | C18 | C0603 | 1 | CGJ3E2X7R1H223K080AA | TDK
8 | 4.7uF | C19 | C0603 | 1 | JMK107BJ475KAHT | Taiyo Yuden
9 | SMAJ26CA-Q | D1 | SMA_L4.2-W2.7-LS5.1-BI | 1 | SMAJ26CA-Q | BOURNS
10 | SL12-E3/5AT | D2 | SMA_L4.3-W2.6-LS5.2-RD | 1 | SL12-E3/5AT | Diodes Incorporated
11 | S1GT-04LC-F | D3 | SMA_L4.4-W2.6-LS5.0-RD | 1 | S1GT-04LC-F | Diodes Incorporated
12 | TBLOCK | J1-1,J1-2,J7,J8 | TBLOCK_2P | 4
13 | 620105131822 | J2,J3,J4,J5 | 620105131822 | 4
14 | 292317-4 | J6 | 2923174 | 1
15 | JUMPER3 | JMP1,JMP2,JMP3,JMP4 | HDR-TH_3P-P2.54-V-M-A | 4 | Jumper3 | null
16 | MH1608-601Y | L1 | L0603 | 1 | MH1608-601Y | BOURNS
17 | LED | LED1 | LED1206-R-RD | 1 | TJ-S3216SW9TGLC2G-A5 | TOGIALED(统佳)
18 | 1k | R0,R16 | R0805 | 2 | CHP0805AFX-1001ELF | Bourns
19 | 0 | R1 | R0603 | 1 | ERJ-3GEY0R00V | PANASONIC
20 | 27 | R2,R3 | R0603 | 2 | CMP0603AFX-27R0ELF | Bourns
21 | 4.7K | R4,R12 | R0603 | 2 | CRCW25124K70JNEG | Vishay
22 | 10K | R5,R6,R7,R9,R10,R14 | R0603 | 6 | CRCW060310K0JNEA | Vishay Intertech
23 | 1.5K | R8,R11 | R0603 | 2 | RC0603FR-071K5L | YAGEO
24 | 47Ω | R13 | R0603 | 1 | CRCW060347R0FKEA | Vishay Intertech
25 | 0.1 | R15 | R0805 | 1 | CRM0805AFX-R100ELF | Bourns
26 | LM7805SX/NOPB | U1 | TO-263-3_L10.2-W8.6-P2.54-LS14.4-TL | 1 | LM7805SX/NOPB | TI(德州仪器)
27 | FT201XS-U | U2 | SSOP-16_L5.0-W4.4-P0.65-LS6.4-BL | 1 | FT201XS-U | FTDI(飞特帝亚)
28 | MCP3428-E/SL | U3 | SOIC-14_L8.7-W3.9-P1.27-LS6.0-BL | 1 | MCP3428-E/SL | Microchip Tech
29 | PCA9543APW | U4 | TSSOP-14_L5.0-W4.4-P0.65-LS6.4-BL | 1 | PCA9543APW | NXP
30 | MPXV5004DP | U5,U6 | SOP-8_L10.7-W10.7-P2.54-LS18.0-BR | 2 | MPXV5004DP | null
31 | BTS70121EPAXUMA1 | U7 | PG-TSDSO-14_L4.9-W3.9-P0.65-LS6.0-BL-EP | 1 | BTS70121EPAXUMA1 | Infineon(英飞凌)
32 | INA2290A1IDGKT | U8 | VSSOP-8_L3.0-W3.0-P0.65-LS4.9-BL | 1 | INA2290A1IDGKT | TI(德州仪器)

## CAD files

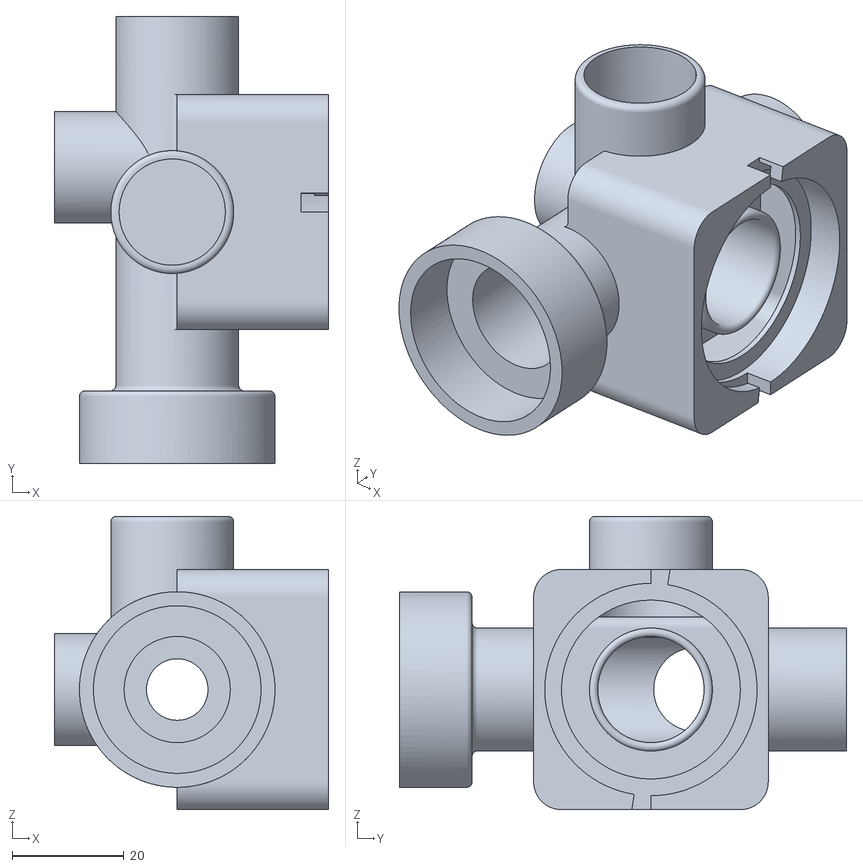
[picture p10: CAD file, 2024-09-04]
3D models/BI001.stl
49.1 x 80.0 x 52.5

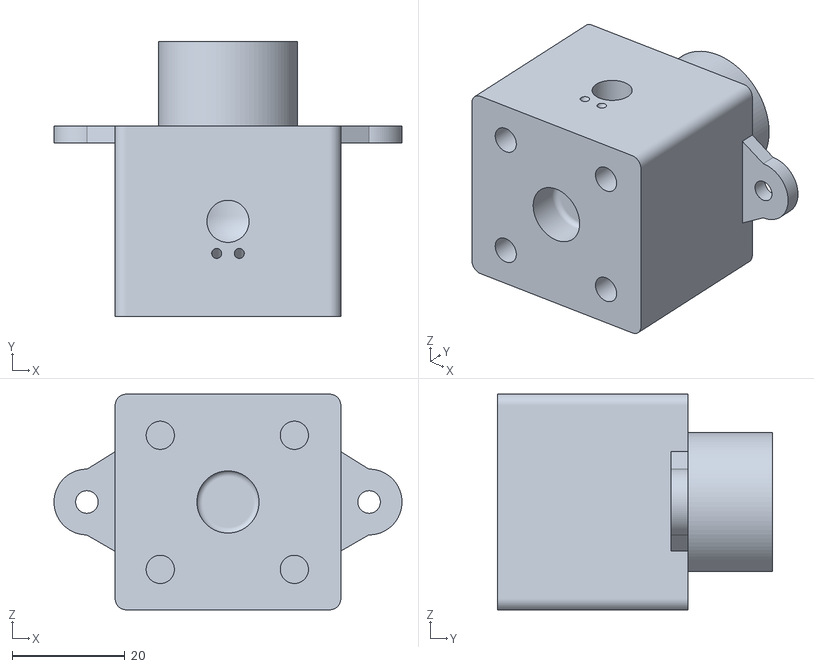
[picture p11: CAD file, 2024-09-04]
3D models/BI013.stl
61.7 x 48.8 x 38.2

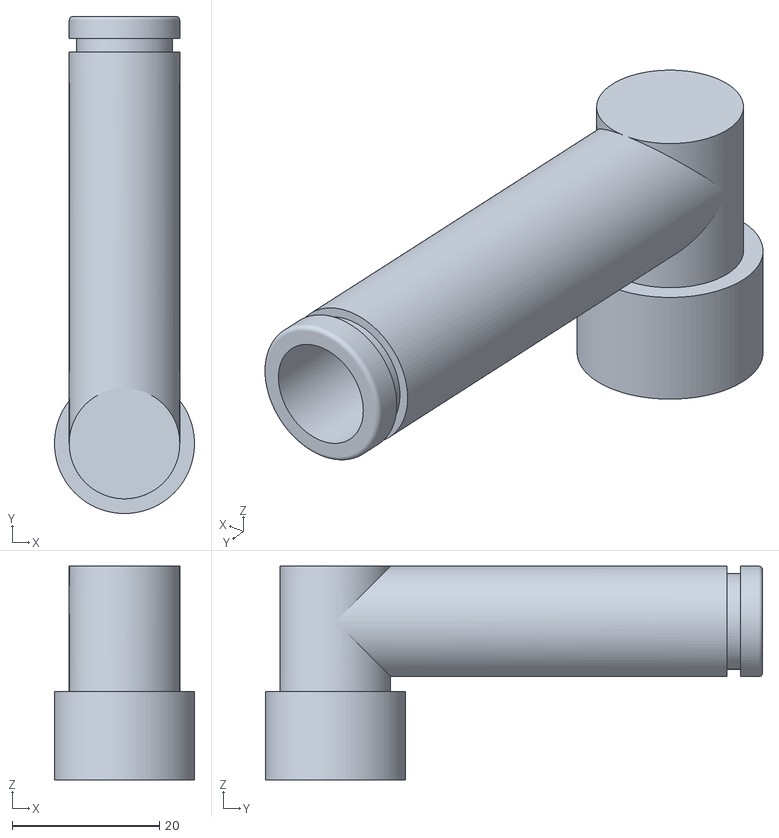
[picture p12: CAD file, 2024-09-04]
3D models/BI008.stl
19.0 x 67.4 x 29.0

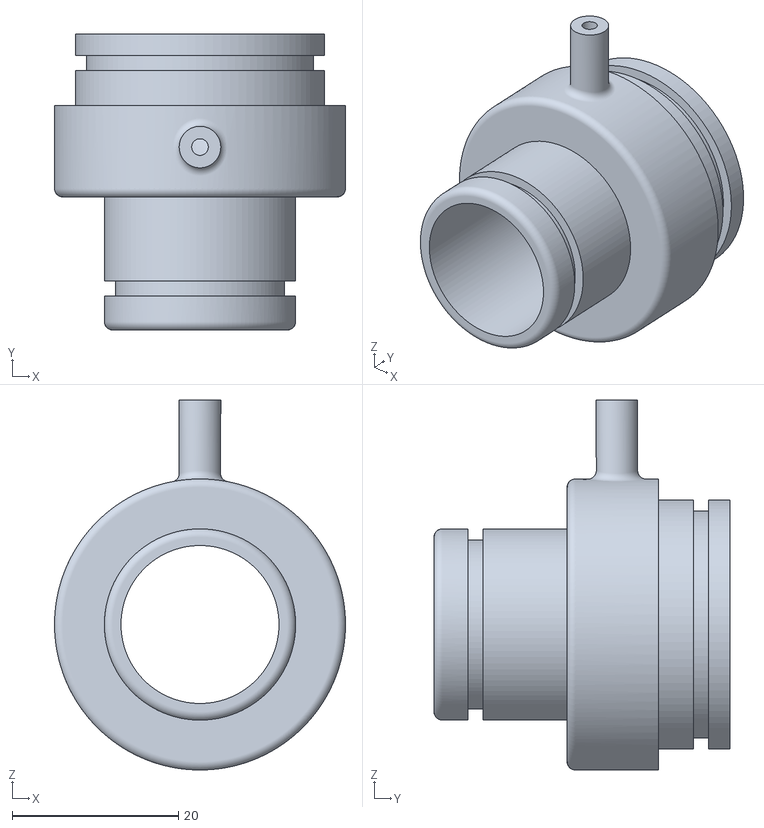
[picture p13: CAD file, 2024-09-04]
3D models/BI003.stl
35.0 x 35.6 x 44.5

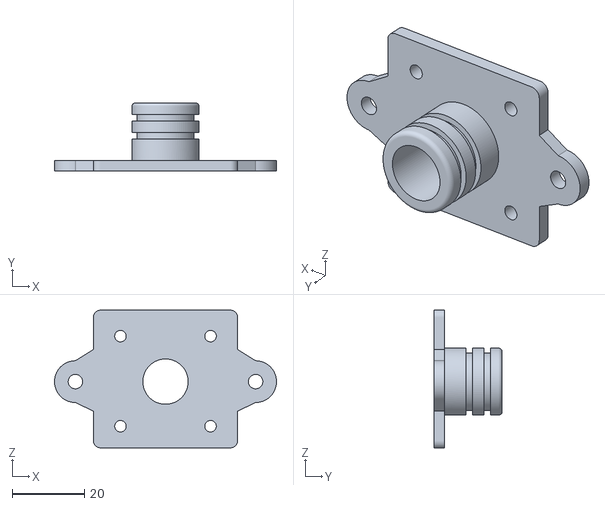
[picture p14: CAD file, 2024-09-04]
3D models/BI016.stl
61.6 x 19.0 x 38.2

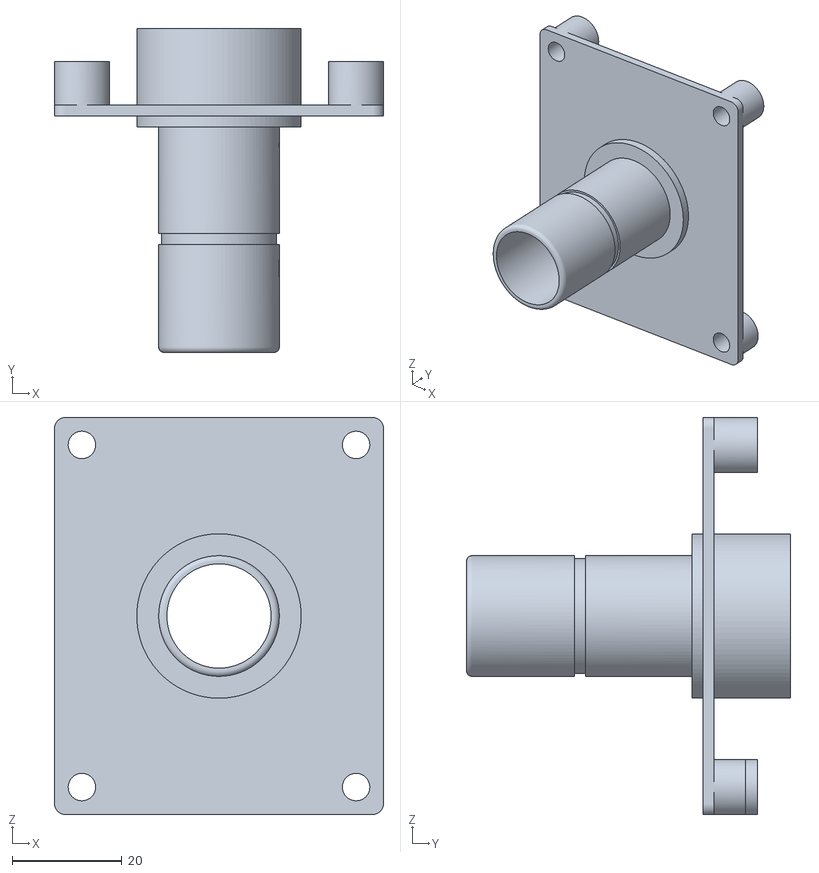
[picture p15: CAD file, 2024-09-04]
3D models/BI004.stl
60.0 x 59.1 x 72.4

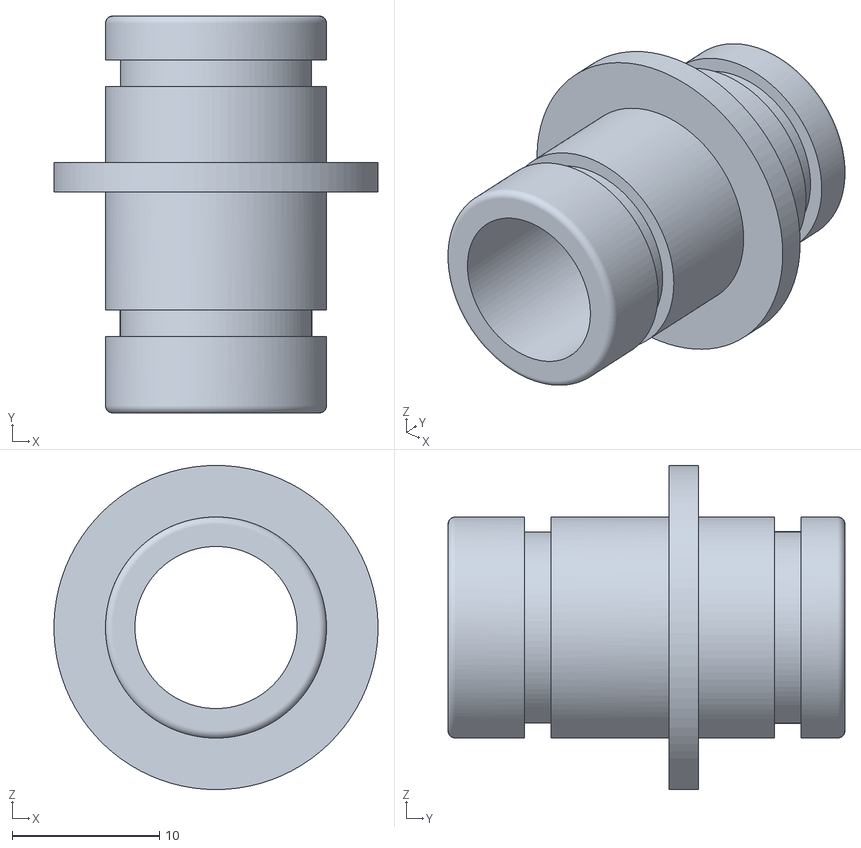
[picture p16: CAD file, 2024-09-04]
3D models/BI007.stl
22.0 x 26.9 x 22.0

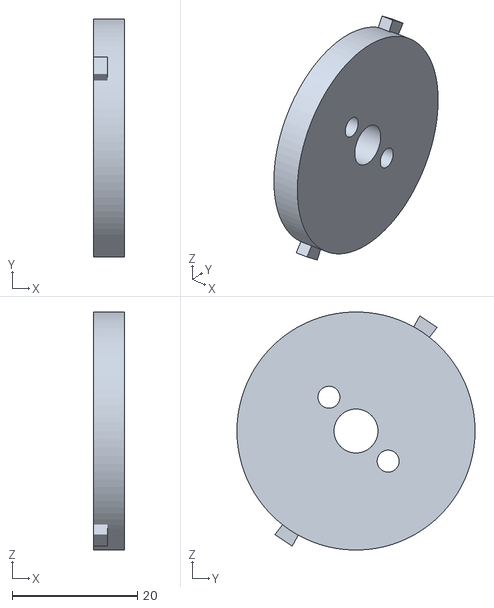
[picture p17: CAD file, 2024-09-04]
3D models/BI005.stl
4.95 x 38.0 x 38.0

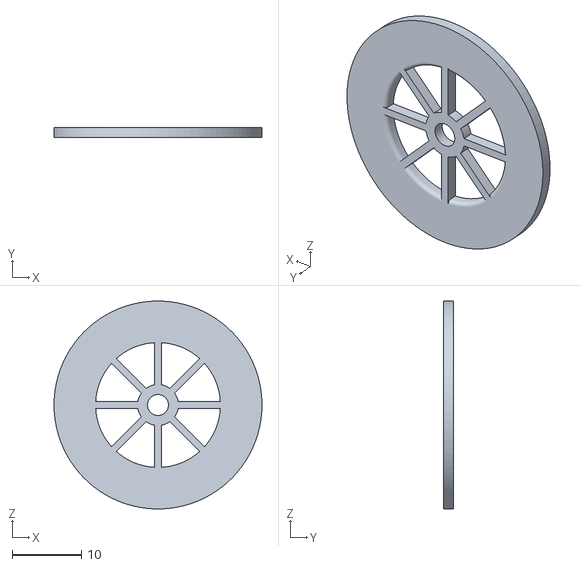
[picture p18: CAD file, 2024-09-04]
3D models/BI002.stl
30.0 x 1.40 x 30.0

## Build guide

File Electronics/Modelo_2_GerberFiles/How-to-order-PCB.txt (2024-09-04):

How to Order PCB

Please refer to:
https://docs.easyeda.com/en/PCB/Order-PCB

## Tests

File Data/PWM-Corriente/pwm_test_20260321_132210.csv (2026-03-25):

tipo | tiempo_ms | pwm_pct | Corriente
CMD | 9528 | START
CMD | 9636 | 0
DATA | 10232 | 0 | 0
DATA | 10238 | 0 | 0
DATA | 10242 | 0 | 0
DATA | 10284 | 0 | 0
DATA | 10293 | 0 | 0
DATA | 10311 | 0 | 0
DATA | 10325 | 0 | 0
DATA | 10360 | 0 | 0
DATA | 10373 | 0 | 0
DATA | 10389 | 0 | 0
DATA | 10405 | 0 | 0
DATA | 10439 | 0 | 0
DATA | 10453 | 0 | 0
DATA | 10471 | 0 | 0
DATA | 10483 | 0 | 0
DATA | 10518 | 0 | 0
DATA | 10534 | 0 | 0
DATA | 10552 | 0 | 0
DATA | 10567 | 0 | 0
DATA | 10599 | 0 | 0
DATA | 10615 | 0 | 0
DATA | 10629 | 0 | 0
DATA | 10647 | 0 | 0
DATA | 10680 | 0 | 0
DATA | 10692 | 0 | 0
DATA | 10709 | 0 | 0
DATA | 10726 | 0 | 0
DATA | 10757 | 0 | 0
DATA | 10772 | 0 | 0
DATA | 10788 | 0 | 0
DATA | 10805 | 0 | 0
DATA | 10840 | 0 | 0
DATA | 10854 | 0 | 0
DATA | 10868 | 0 | 0
DATA | 10883 | 0 | 0
DATA | 10919 | 0 | 0
DATA | 10931 | 0 | 0
DATA | 10948 | 0 | 0
DATA | 10965 | 0 | 0
DATA | 11000 | 0 | 0
DATA | 11016 | 0 | 0
DATA | 11030 | 0 | 0
DATA | 11044 | 0 | 0
DATA | 11078 | 0 | 0
DATA | 11092 | 0 | 0
DATA | 11109 | 0 | 0
DATA | 11127 | 0 | 0
DATA | 11159 | 0 | 0
DATA | 11174 | 0 | 0
DATA | 11190 | 0 | 0
DATA | 11206 | 0 | 0
DATA | 11235 | 0 | 0
DATA | 11251 | 0 | 0
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

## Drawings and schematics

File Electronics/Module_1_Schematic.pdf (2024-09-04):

## Alimentaci n y comunicaci n al exterior

## Regulador LDO de 3.3v @ 300 mA

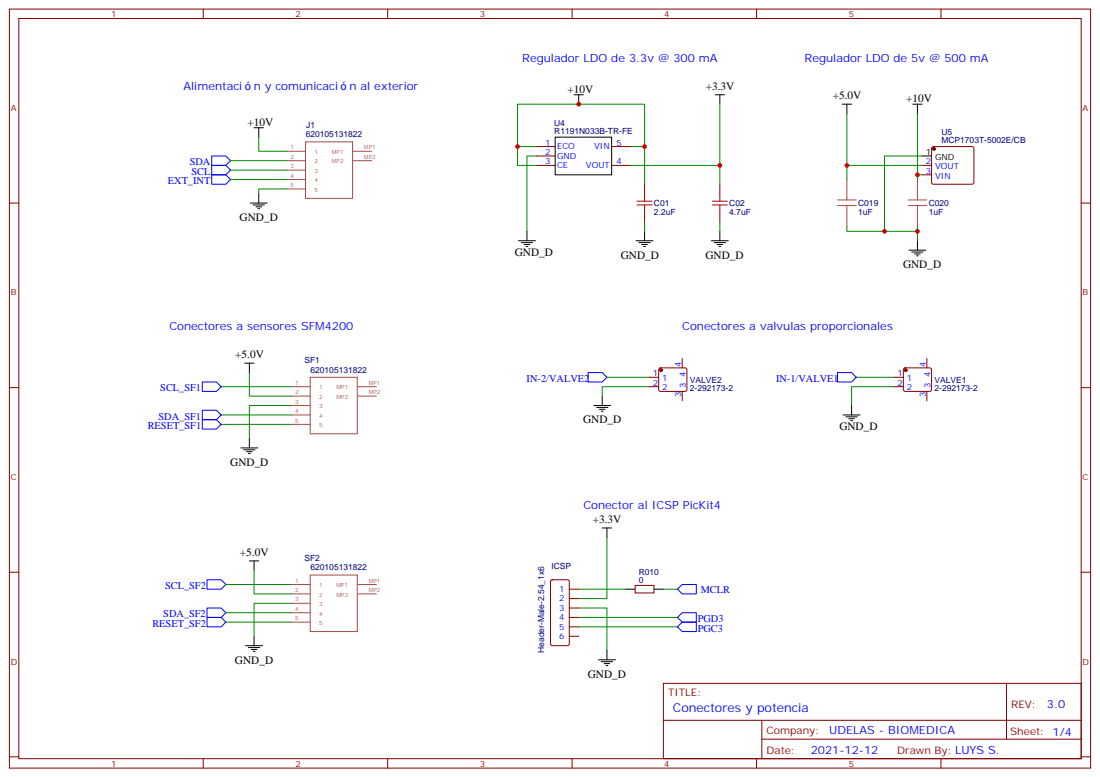
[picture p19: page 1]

Regulador LDO de 5v @ 500 mA

## Microcontrolador Principal

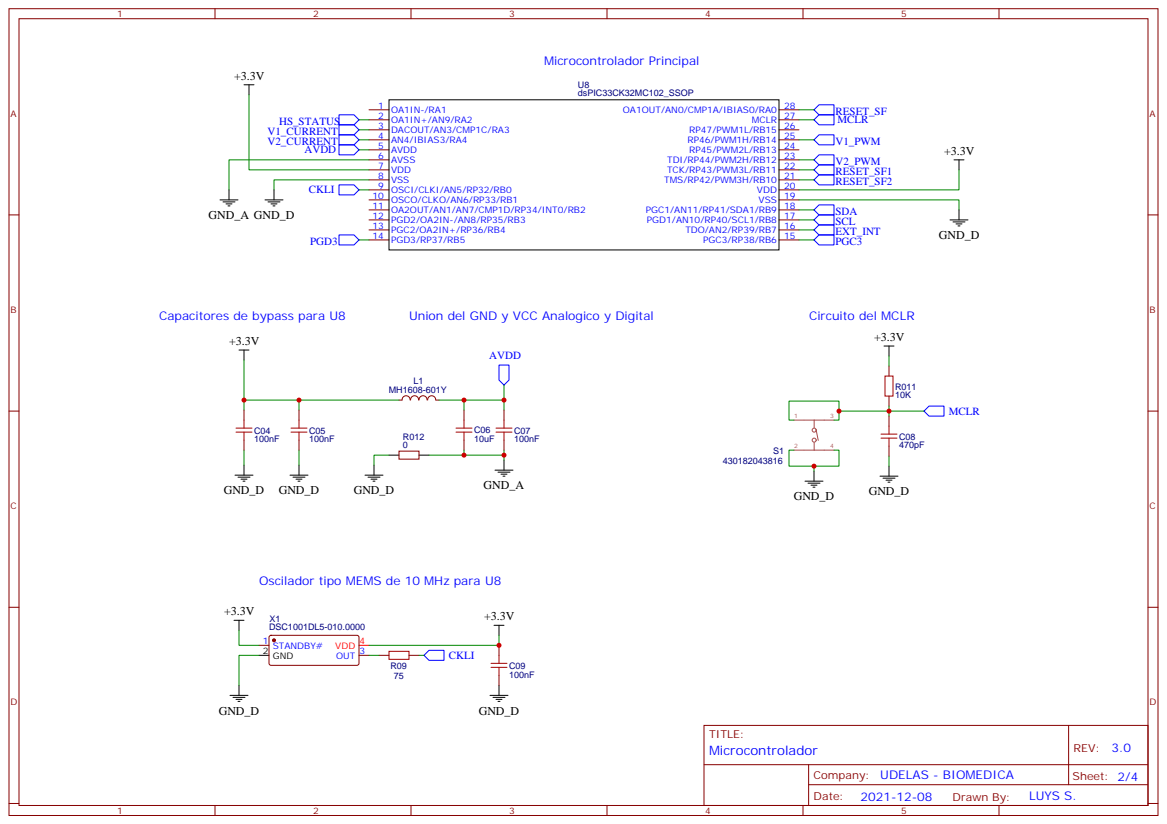
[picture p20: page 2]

Capacitores de bypass para U8

Oscilador tipo MEMS de 10 MHz para U8

## Mosfet High Side Switch

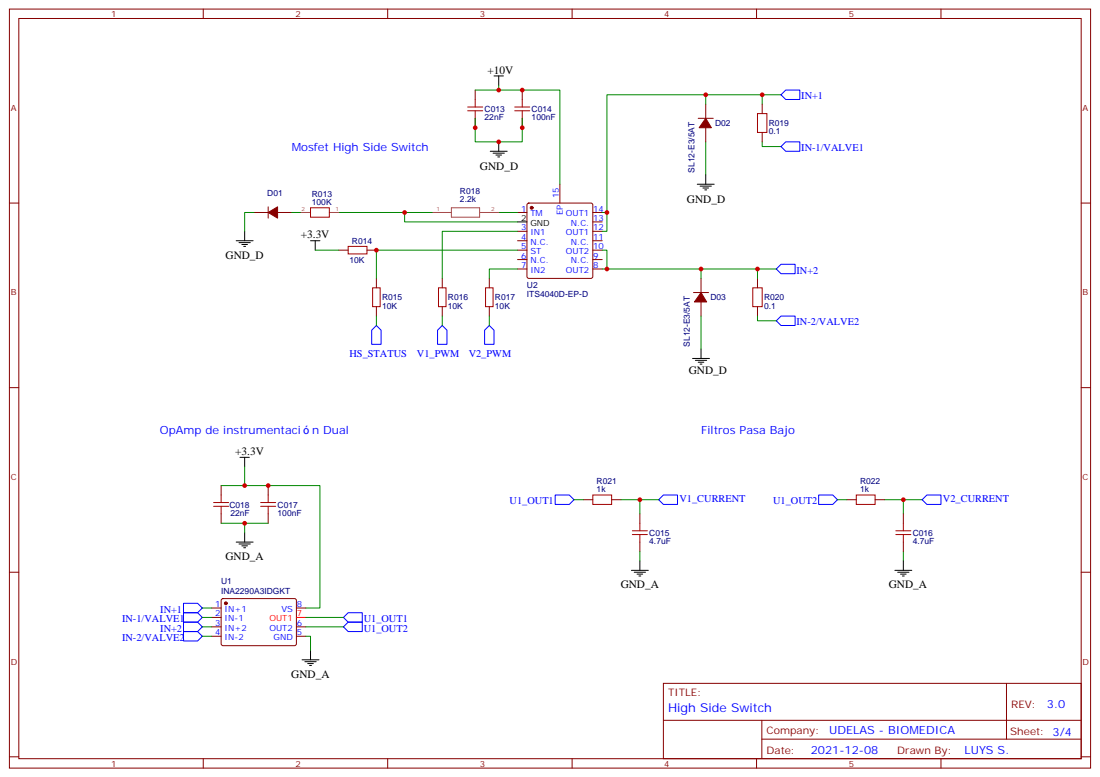
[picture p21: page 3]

I2C pull-ups | Capacitores de bypass para U3, U7, P1, P2 | Switch I2C

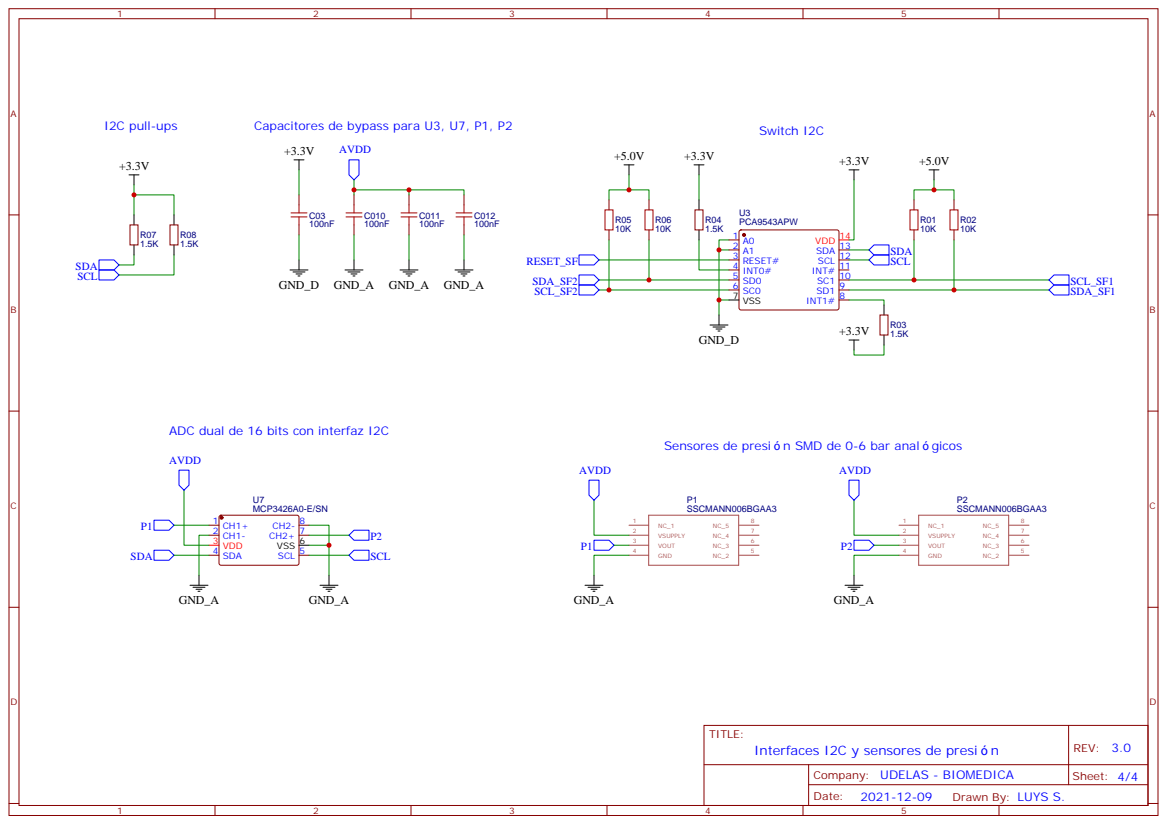
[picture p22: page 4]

SC1 10 INT# 11 SCL 12 SDA 13 VDD 14

ADC dual de 16 bits con interfaz I2C

Sensores de presi n SMD de 0-6 bar anal gicos

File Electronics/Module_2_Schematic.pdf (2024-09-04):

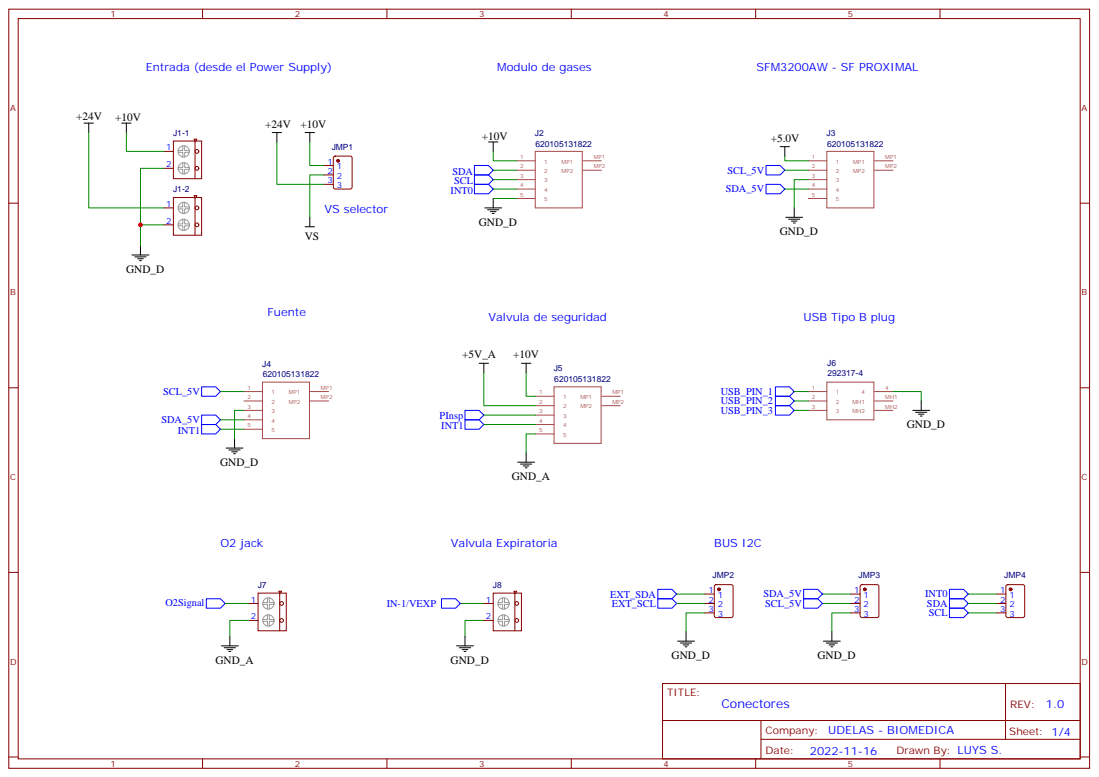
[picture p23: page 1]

Entrada (desde el Power Supply)

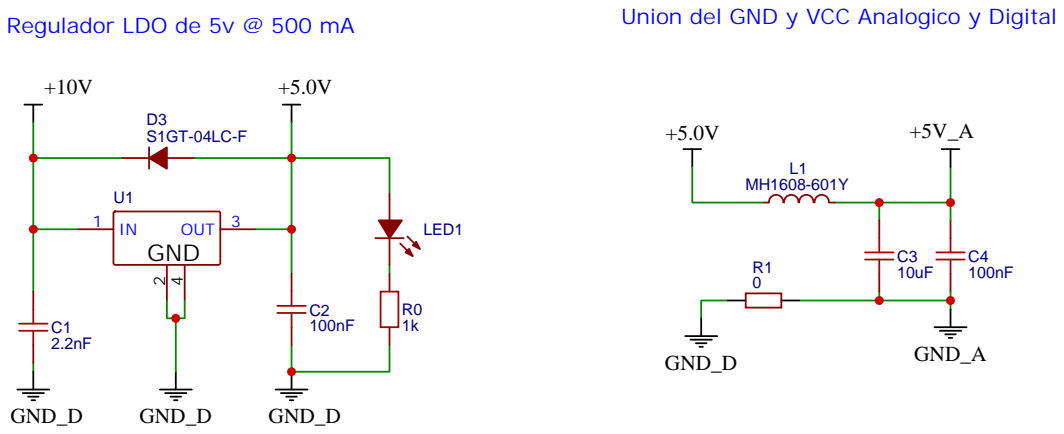
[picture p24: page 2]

Union del GND y VCC Analogico y Digital

Regulador LDO de 5v @ 500 mA

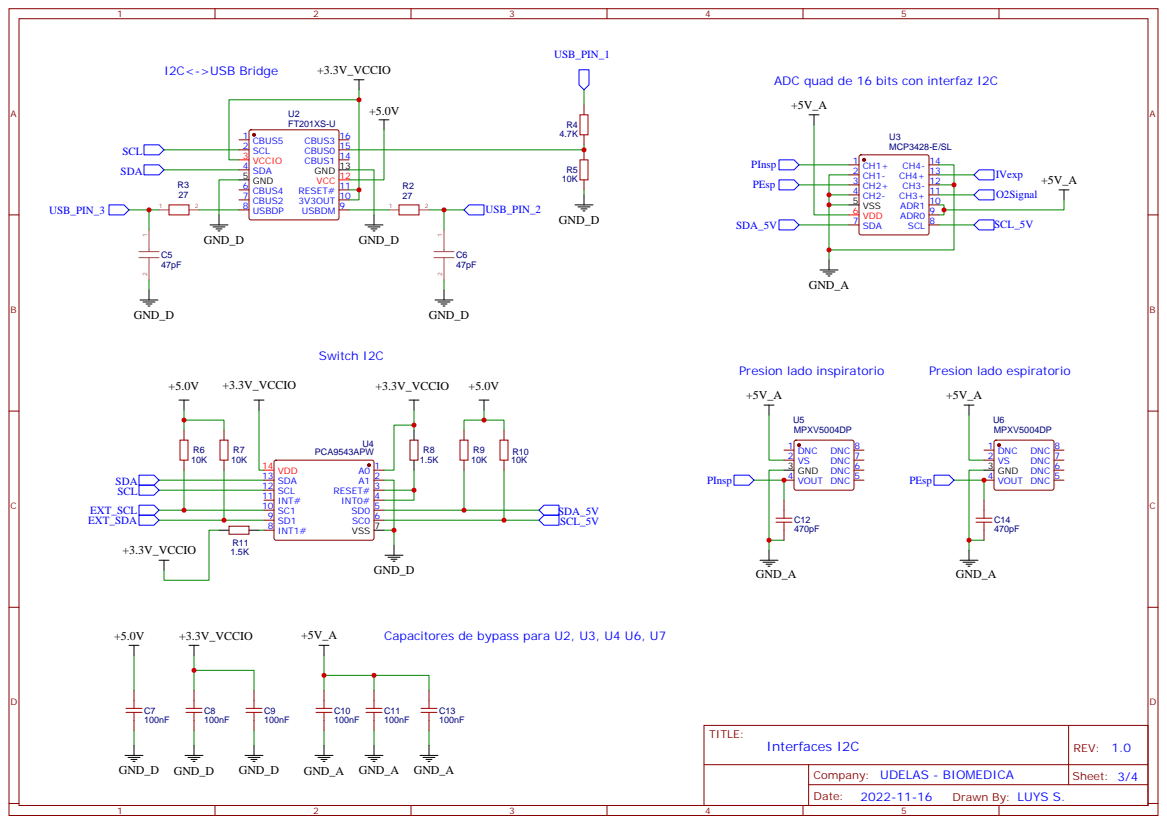
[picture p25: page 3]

ADC quad de 16 bits con interfaz I2C

Capacitores de bypass para U2, U3, U4 U6, U7

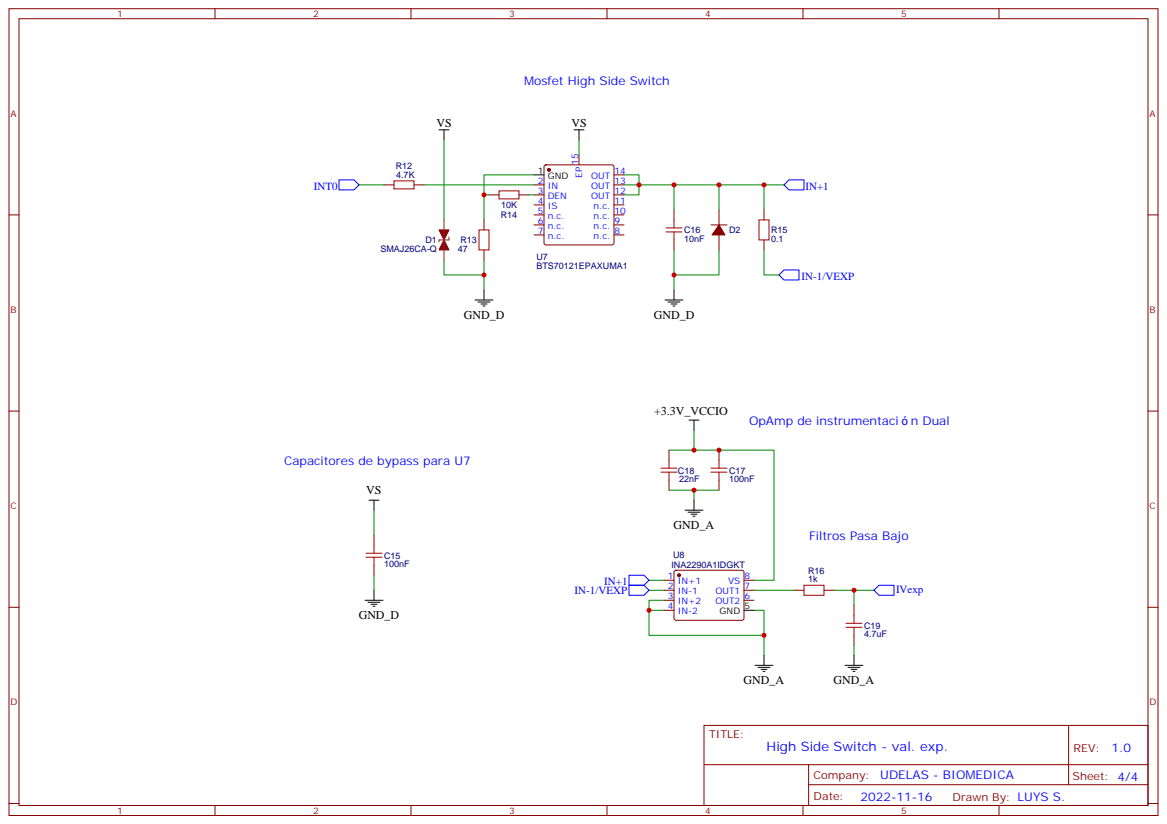
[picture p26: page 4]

Mosfet High Side Switch

OpAmp de instrumentaci n Dual

Capacitores de bypass para U7

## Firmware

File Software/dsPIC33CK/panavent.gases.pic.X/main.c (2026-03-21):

#include <math.h>
#include "main.h"
#include <xc.h>
#define FCY 60000000UL
#include <libpic30.h>
#include "comun.h"
#include "app.h"
#include "comm.h"
#include "monitorPowerSupply.h"
#include "../panavent.hardware.drivers.X/mcc_generated_files/system/system.h"
#include "../panavent.hardware.drivers.X/timer3Controller.h"
#include "../panavent.hardware.drivers.X/pca9543apw_interface.h"
#include "../panavent.hardware.drivers.X/mcp342x_interface.h"
#include "../panavent.mezclador.X/mezclador.h"
#include "../panavent.valexp.X/valvulaExpiratoria.h"
#include "../panavent.hardware.drivers.X/mcc_generated_files/pwm/sccp4.h"
#include "../panavent.hardware.drivers.X/sfm_interface.h"

float t1 = 0;
float t2 = 0;

#define TICKS_SEND_DATA     20
#define TICKS_GET_COMMAND   1000
#define TICKS_MCP           250

volatile uint16_t cnt_timing_mcp = 0;
volatile uint16_t cnt_timing_ventilacion = 0;
volatile uint16_t cnt_timing_send_data = 0;
volatile uint16_t cnt_timing_get_command = 0;

static uint8_t pidTuningIndex = 0xFF;
uint8_t mcp2ch = 1;
PIDrequest presionPIDreq;
float presionInspM = 1;
float presionInspB = 0;
float presionExpM = 1;
float presionExpB = 0;
volatile uint8_t FLAG = 0x00;

#define TIMING_MCP_FLAG                     CHECKBIT(FLAG,2)
#define TIMING_CLEAR_MCP_FLAG               CLEARBIT(FLAG,2)
#define TIMING_SET_MCP_FLAG                 SETBIT(FLAG,2)
#define CAPTURAR_VTI_FLAG                   CHECKBIT(FLAG,4)
#define CLEAR_CAPTURAR_VTI_FLAG             CLEARBIT(FLAG,4)
#define SET_CAPTURAR_VTI_FLAG               SETBIT(FLAG,4)
#define TIMING_GET_APP_COMMAND_FLAG         CHECKBIT(FLAG,5)
#define TIMING_CLEAR_APP_COMMAND_FLAG       CLEARBIT(FLAG,5)
#define TIMING_SET_COMMAND_FLAG             SETBIT(FLAG,5)
#define TIMING_SEND_DATA_FLAG               CHECKBIT(FLAG,6)
#define TIMING_CLEAR_SEND_DATA_FLAG         CLEARBIT(FLAG,6)
#define TIMING_SET_SEND_DATA_FLAG           SETBIT(FLAG,6)

ErrorCode error;
volatile MainState gState = ST_BOOT;

 
static AppVentilacionParams ventilacionParams;
static AppVentilacionData ventilacionData;

static volatile bool hayInstruccionPendiente = false;
static volatile uint8_t instruccionPendiente = 0;

static volatile bool hayConstantesPIDPendientes = false;
static volatile bool hayCalibracionPendiente = false;
static volatile bool hayPWMPendiente = false;

static AppConstantesPID constantesPIDRx;
static AppCalibracionData calibracionRx;
static AppPWMData pwmRx;

int main(void) {
    while (1) {
        if (gState == ST_BOOT) {
            if (inicializacion()) {
                app.sendError(INIT_OK);
                cambiarEstado(ST_IDLE);
            } else {
                app.sendError(error);
                __delay_ms(1000);
            }
        } else {
            
            getAppCommands();
            procesarEventosApp();
            sendAppData();

            switch (gState) {
                case ST_IDLE:
                    monitorPowerSuply.cerrarValvulaSeguridad(false);
                    break;

                case ST_VENTILANDO:
                    ejecutarVentilacion();
                    break;

                case ST_PID_TUNING:
                    ejecutarPidTuning();
                    break;

                case ST_MANUAL_PWM:
                    ejecutarManualPWM();
                    break;

                case ST_RESET:
                    ejecutarReset();
                    break;

                default:
                    ejecutarReset();
                    break;
            }
        }
    }
}

static void cambiarEstado(MainState nuevoEstado) {
    if (gState == nuevoEstado) return;
    onExitEstado((MainState)gState);
    gState = nuevoEstado;
    onEnterEstado(nuevoEstado);
}

static void onEnterEstado(MainState estado) {
    switch (estado) {
        case ST_VENTILANDO:
            resetVariablesVentilacion();
            break;

        case ST_MANUAL_PWM:
            mezclador.startManualPWM();
            break;

        case ST_PID_TUNING:
            pidTuningIndex = 0xFF;
            break;

        default:
            break;
    }
}

static void onExitEstado(MainState estado) {
    switch (estado) {
        case ST_MANUAL_PWM:
            mezclador.stopManualPWM();
            break;

        case ST_PID_TUNING:
            pidTuningIndex = 0xFF;
            break;

        default:
            break;
    }
}

static void getAppCommands(void) {
    if (!TIMING_GET_APP_COMMAND_FLAG) return;

    monitorPowerSuply.getInfoCarga();
    comm.getCommands();
    TIMING_CLEAR_APP_COMMAND_FLAG;
}

static void procesarEventosApp(void) {
    if (hayInstruccionPendiente) {
        switch (instruccionPendiente) {
            case 0x01: cambiarEstado(ST_RESET); break;
            case 0x02: cambiarEstado(ST_VENTILANDO); break;
            case 0x03: cambiarEstado(ST_PID_TUNING); break;
            case 0x05: cambiarEstado(ST_MANUAL_PWM); break;
            case 0x06: cambiarEstado(ST_IDLE); break;
            default: break;
        }
        hayInstruccionPendiente = false;
    }

    if (hayConstantesPIDPendientes) {
        procesarConstantesPID(false);
        hayConstantesPIDPendientes = false;
    }

    if (hayCalibracionPendiente) {
        procesarCalibracion();
        hayCalibracionPendiente = false;
    }
}

static void ejecutarVentilacion(void) {
    if (TIMING_MCP_FLAG) {
        leerMCP2();
        TIMING_CLEAR_MCP_FLAG;
    }

    monitorPowerSuply.cerrarValvulaSeguridad(true);

    if (ventilacionData.fase == 1) {
        if (!CAPTURAR_VTI_FLAG) SET_CAPTURAR_VTI_FLAG;
        valvulaExpiratoria.cerrar();
    } else if (ventilacionData.fase == 2) {
        if (CAPTURAR_VTI_FLAG) {
            ventilacionData.vti = ventilacionData.volumen;
            CLEAR_CAPTURAR_VTI_FLAG;
        }
        valvulaExpiratoria.controlPeep(ventilacionParams.peep);
    }

    mezclador.fm = getFlujoMeta();
    mezclador.cm = ventilacionParams.fiO2;

    if (mezclador.mezclar()) {
        ventilacionData.flujo = mezclador.data;
        t2 = (float)cnt_timing_ventilacion * TIMER3_PERIOD;
        ventilacionData.deltaT = (t2 - t1);
        ventilacionData.volumen += (ventilacionData.deltaT) * (ventilacionData.flujo / 60.0f) * 1000.0f;
        t1 = t2;
    }

    if (sfmProxi.leerFlujo()) {
        ventilacionData.flujoProximal = sfmProxi.flow;
    }
}

static void ejecutarPidTuning(void) {
    monitorPowerSuply.cerrarValvulaSeguridad(true);

    if (comm.getCommand(true, APP_CMD_PROCESOS_CONSTANTES_PID, 0)) {
        if (hayConstantesPIDPendientes) {
            procesarConstantesPID(true);
            pidTuningIndex = constantesPIDRx.indice;
            hayConstantesPIDPendientes = false;
        }
    }

    switch (pidTuningIndex) {
        case 3:
            if (TIMING_MCP_FLAG) {
                leerMCP2();
                mezclador.cl = (ventilacionData.fiO2 * 3065.9f - 3.6271f) / 100.0f;
                TIMING_CLEAR_MCP_FLAG;
            }
            mezclador.mezclar();
            break;

        case 4:
            mezclador.mezclarAire();
            break;

        case 5:
            mezclador.mezclarOxigeno();
            break;
    }
}

static void ejecutarManualPWM(void) {
    monitorPowerSuply.cerrarValvulaSeguridad(true);

    if (comm.getCommand(true, APP_CMD_PROCESOS_SET_PWM, 0)) {
        if (hayPWMPendiente) {
            if (pwmRx.oxigeno) {
                mezclador.setPWMOxigeno(pwmRx.porcentaje);
            } else {
                mezclador.setPWMAire(pwmRx.porcentaje);
            }
            hayPWMPendiente = false;
        }
    }
}

static void ejecutarReset(void) {
    monitorPowerSuply.cerrarValvulaSeguridad(false);
    mezclador.stopManualPWM();
    resetVariablesVentilacion();
    app.sendError(RESETING);
    cambiarEstado(ST_BOOT);
}

static void resetVariablesVentilacion(void) {
    cnt_timing_send_data = 0;
    cnt_timing_ventilacion = 0;
    t1 = 0.0f;
    t2 = 0.0f;
    ventilacionData.volumen = 0.0f;
    ventilacionData.vti = 0.0f;
    ventilacionData.vte = 0.0f;
    ventilacionData.deltaT = 0.0f;
    ventilacionData.ciclo = 0;
    ventilacionData.fase = 1;
    CLEAR_CAPTURAR_VTI_FLAG;
}

static void sendAppData(void) {
    if (!TIMING_SEND_DATA_FLAG) return;

    switch (gState) {
        case ST_PID_TUNING:
            app.sendData(mezclador.data);
            break;
        case ST_MANUAL_PWM:
            app.sendData(mezclador.data);
            break;
        case ST_VENTILANDO:
            app.sendVentilacionData(ventilacionData);
            break;

        default:
            break;
    }

    TIMING_CLEAR_SEND_DATA_FLAG;
}

static bool inicializacion(void) {
    SYSTEM_Initialize();

    app.onVentilacionParams = &Main_OnVentilacionParams;
    app.onConstantesPID = &Main_OnConstantesPID;
    app.onCalibracionData = &Main_OnCalibracionData;
    app.onPWMData = &Main_OnPWMData;
    app.onInstruccion = &Main_OnInstruccion;
    app.inicializar();

    while (true) {
        if (comm.sendCommandAndWait(APP_CMD_PROTOCOLO_PING, APP_CMD_PROTOCOLO_ACK)) {

            timer3Controller.inicializar();
            timer3Controller.agregarCallback(&timingTimerCallBack, TIMER3_PERIOD);

            error = mezclador.inicializar();

            if (error == NO_ERROR) {
                uint8_t i = 0;

                while (i < 7) {
                    uint8_t args[] = {i};
                    hayConstantesPIDPendientes = false;

                    if (comm.sendCommandAndWaitWithArgs(
                            APP_CMD_PROCESOS_GET_CONSTANTES_PID,
                            APP_CMD_PROCESOS_CONSTANTES_PID,
                            args,
                            1)) {

                        if (hayConstantesPIDPendientes) {
                            procesarConstantesPID(false);
                            hayConstantesPIDPendientes = false;
                        } else {
                            error = GET_PID_PARAM_ERROR;
                            app.sendError(error);
                            break;
                        }
                    } else {
                        error = GET_PID_PARAM_ERROR;
                        app.sendError(error);
                        break;
                    }

                    i++;
                }

                if (error == NO_ERROR) {
                    i = 0;

                    while (i < 8) {
                        uint8_t args[] = {i};
                        hayCalibracionPendiente = false;

                        if (comm.sendCommandAndWaitWithArgs(
                                APP_CMD_PROCESOS_GET_CALIBRACION,
                                APP_CMD_PROCESOS_CALIBRACION,
                                args,
                                1)) {

                            if (hayCalibracionPendiente) {
                                procesarCalibracion();
                                hayCalibracionPendiente = false;
                            } else {
                                error = GET_CALIBRACION_ERROR;
                                app.sendError(error);
                                break;
                            }
                        } else {
                            error = GET_CALIBRACION_ERROR;
                            app.sendError(error);
                            break;
                        }

                        i++;
                    }
                }
            }

            valvulaExpiratoria.inicializar();

            //if (!sfmProxi.inicializar()) {
            //    error = SFM_PROX_ERROR;
            //}

            if (error == NO_ERROR) {
                return true;
            }
        }

        __delay_ms(10000);
    }

    return false;
}
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

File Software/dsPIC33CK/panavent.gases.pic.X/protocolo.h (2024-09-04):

#ifndef PROTOCOLO_H
#define	PROTOCOLO_H

#include "mcc_generated_files/i2c_host/i2c1.h"  

#define CHECKBIT(B, BIT)             ((B >> BIT) & 1)==1
#define CLEARBIT(B,BIT)              B &= ~(1 << BIT)
#define SETBIT(B,BIT)                B |= 1 << BIT
#define TOGGLE(B,BIT)                B ^= 1 << BIT

/*      X       X       XXX         XXX    */
/*      ON      RESET   SUB-MODO    MODO   */



#define _MODO_TIPO(B)                    (B & 0x38) >> 3
#define _RESET_MODO(B)                   (B & 0xC7)  

/*MODO*/
#define _MVC(B)                         (B & 0x07) == 0x01 
#define _MPC(B)                         (B & 0x07) == 0x02   
#define _MSERV(B)                       (B & 0x07) == 0x03   
#define _IS_MVENT(B)                    ((_MVC(B)) || (_MPC(B))) 
#define _IS_MSERV(B)                    _MSERV(B)  

/*MODOS DE VOLUMEN*/
#define _MVCSQR(B)                      _MODO_TIPO(B) == 0x01   
#define _MVCSIN(B)                      _MODO_TIPO(B) == 0x02   
#define _MVCDES(B)                      _MODO_TIPO(B) == 0x03 

/*MODOS DE PRESION*/
#define _MPCDEF(B)                      _MODO_TIPO(B) == 0x01

/*MODOS DE SERVICIO*/
#define _KPID(B)                        _MODO_TIPO(B) == 0x01
#define _ADJ(B)                         _MODO_TIPO(B) == 0x02 
#define _CAL(B)                         _MODO_TIPO(B) == 0x03 

#define _ISACK(B)                       (B==0xFF)
#define _ISOFF(B)                       (B==0x00)
#define _ON(B)                          (!_ISACK(B) && CHECKBIT(B,7) && (_IS_MVENT(B) || _IS_MSERV(B))) 
#define _CLEAR_RESET(B)                 CLEARBIT(B,6) 
#define _RESET(B)                       (!_ISACK(B) && CHECKBIT(B,6) && (_IS_MVENT(B) || _IS_MSERV(B))) 
 

typedef enum 
{
    SFM_O2_OK=1,
    SFM_AIRE_OK=2,
    SFM_PROX_OK=3,
    MCP3426_OK=4,
    MCP3428_OK=5,
    VALVE_AIRE_OK=6,
    CANAL_PCA9543APW_OK = 7,
    DIS_PCA9543APW_OK = 8,
    MCPMODULO1_OK = 9,
    MCPMODULO2_OK = 10,
    VALVE_O2_OK=11,
    VALVE_EXP_OK=12,  
    INIT_OK=13, 
    MOMPS_OK = 14,
    SFM_O2_ERROR=128,    
    SFM_AIRE_ERROR=129,    
    SFM_PROX_ERROR=130,    
    MCP3426_ERROR=131,    
    MCP3428_ERROR=132,    
    VALVE_AIRE_ERROR=133,
    INIT_ERROR=134,    
    CANAL_PCA9543APW_ERROR = 135,   
    DIS_PCA9543APW_ERROR = 136,   
    MCPMODULO1_ERROR = 137,   
    MCPMODULO2_ERROR = 138,    
    VALVE_O2_ERROR=139,    
    VALVE_EXP_ERROR=140,
    RESETING=141,
    MOMPS_ERROR = 142
            
} ErrorCode;

enum IE {
    IE11,
    IE12,
    IE13,
    IE14,
    IE21,
    IE31,
    IE41
};

typedef enum TIPO_PARAM {
    P_FA=0,
    P_FO=1,
    P_PS=2,
    P_FLUJO_PROXIMAL=3,
    P_VI=4,
    P_PEEP=5,
    P_VALVE_AIRE=6,
    P_VALVE_OXI=7,
    P_EXP=8
} TipoParam;
 

typedef struct {
    float volumen;
    float flujo; 
    float fiO2;
    float fr;
    enum IE ie;
    float presion;
    float peep;
    float pi;
    float tt;
    float ti;
    float te;
    
    float kp;
    float ki;
    float kd;
    float maxOutput;
    float minOutput;
    float emaAlpha;
    
    float qi;
    float fi;
    
    float   param;
    TipoParam tipoParam;
    
    float m;
    float b;
    
} Parametros;
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

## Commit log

2024-09-04 3D Models
    [BI001.stl, BI002.stl, BI003.stl, BI004.stl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]
2026-03-21 Add comm module and refactor app
    Introduce a new comm module (comm.c / comm.h) that centralizes I2C framing, parsing and send/wait logic. Move low-level protocol handling out of app.c, replace it with a callback-based interface and 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
2026-03-25 Add PWM current datasets and update builds
    Add PWM-Corriente datasets (prbs and synthetic .xlsx) and a large pwm_test CSV for PWM vs. current analysis. Include a new queuelogs/debugtool.txt. Update dsPIC33CK build artifacts and project config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
    [dataset_prbs_pwm_corriente_10k.xlsx, dataset_sintetico_pwm_corriente_10k.xlsx, pwm_test_20260321_132210.csv]
